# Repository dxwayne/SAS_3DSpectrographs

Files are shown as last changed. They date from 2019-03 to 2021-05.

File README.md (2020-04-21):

# SAS_3DSpectrograps

Next Meeting: 7 April 2020 Meeting ID: 855 133 831

Experiments with spectroscopy using 3D printing.

Zoom meeting and resources, results for this work.

Experiments with spectroscopy using 3D printing.

[Link to Videos on Wiki](https://github.com/dxwayne/SAS_3DSpectrographs/wiki)

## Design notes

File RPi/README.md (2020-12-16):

Raspberry Pi
============

Included herein are various interesting parts and code for the RPi.

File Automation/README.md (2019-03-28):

Good article about motors
--------------------------
https://www.instructables.com/id/Complete-Motor-Guide-for-Robotics/

Robot Parts - example (no experience with company)
https://www.robotshop.com/en/10v-05a-planetary-gear-bipolar-stepper-motor.html#Dimensions
35STH Hybrid Stepping Motor

400 steps per rev
27:1 reduction  = 0.03 degrees per step.

https://ldomotors.manufacturer.globalsources.com/si/6008840349362/pdtl/Stepping-motor/1164961550/nema14-35mm-2phase-hybrid-stepper-motor.htm?state_filt=cn_cnfuj?source=coyname_l4dd
0.9 degree step,

400 steps per rev
27:1 reduction  = 0.03 degrees per step.

https://www.robotshop.com/en/actobotics-84t-aluminum-hub-gear-05.html#Dimensions
Product Code : RB-Sct-682  84T 1/4 inch thick 32 pitch 0.5 bore 2.688 OD

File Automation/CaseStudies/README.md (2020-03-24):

Automation Case Studies
=======================

Collection of basic case studies to allow development of a common architecure of hardware
software for instrument and site automation.

1) Focus on each task to be done like turn the cal lamp on,
   turn the call lamp off, etc,

2) To develop a few bits of code for each function that will include
   a class/code for that task to run in both python and C++.

3) Each task will have messages for actions and to report both
   status, warnings and errors.

I want to ignore the transport layer as much as possible. I like
RS-232 for the OTA and any other standard for the rest of the world.

Sugest dividing the world into telescope/instrumentation, observatory
control, and then to the sensors for temperature, humidity and
other factors as they come along.

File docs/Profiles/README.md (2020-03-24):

Printing Profile Collection
============================

Put the material, vendor etc in this document as a table of contents.

Tony Rodda - Cura Wanhao i3 Plus, with modest mods and some maintenance over time.

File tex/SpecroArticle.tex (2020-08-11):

\documentclass[letter,11pt,oneside]{article}
%%% HEREHEREHERE
%%% APPENDIX
%%% (insert (format "%s" (buffer-file-name)))
% /home/wayne/git/external/SAS_3DSpectrographs/tex/SpecroArticle.tex
%%% (occur "\\(\\\\[a-z]*section\\|appendix\\|input\\|\\<include\\>\\)")

%%\documentclass[11pt,twocolumn]{article}
%%\usepackage[inline]{asymptote}       %% Inline asymptote diagrams
%%\usepackage{wglatex}                 %% Use this one and kill others.
\usepackage{color}                     %% colored letters {\color{red}{{text}}
\usepackage{fancyhdr}                  %% headers/footers
%%\usepackage{fancyvrb}                %% headers/footers
\usepackage{datetime}                  %% pick up tex date time 
\usepackage{lastpage}                  %% support page of ...lastpage
\usepackage{times}                     %% native times roman fonts
\usepackage{textcomp}                  %% trademark
\usepackage{amssymb,amsmath}           %% greek alphabet
\usepackage{parskip}                   %% blank lines between paragraphs, no indent
\usepackage{shortvrb}                  %% short verb use for tables
\usepackage{lscape}                    %% landscape for tables.
\usepackage{longtable}                 %% permit tables to span pages wg-longtable
\usepackage{multicol}                  %% Enhance footnotes/endnotes
\usepackage{url}                       %% Make URLs uniform and links in PDFs
\usepackage{enumerate}                 %% Allow letters/decorations for enumerations
\usepackage{endnotes}                  %% Enhance footnotes/endnotes
\usepackage{listings}                  %% Make URLs uniform and links in PDFs
\pdfadjustspacing=1                    %% force LaTeX-like character spacing
\usepackage{geometry}                  %% allow margins to be relaxed
%%\usepackage{wrapfig}                 %% permit wrapping figures.
%%\usepackage{subfigure}               %% images side by side.
\geometry{margin=1in}                  %% Allow narrower margins etc.
\usepackage[T1]{fontenc}               %% Better Verbatim Font.
\renewcommand*\ttdefault{txtt}        %% 
\usepackage[colorlinks=true]{hyperref} %% Make huperlinks within a PDF
\usepackage{natbib}                    %% bibitems

%% include background image (wg-document-page-background) 

\usepackage{graphic
x}            %% Include pictures into a document
%% (wg-texdoc-inserttikz)

\usepackage{pgf,tikz,pgfplots}
\pgfplotsset{compat=1.15}
\usepackage{mathrsfs}

\usetikzlibrary{decorations.pathreplacing}
\usetikzlibrary{decorations.markings}
\usetikzlibrary{calc}
\usetikzlibrary{arrows}
\pgfplotsset{every tick label/.append style={font=\tiny}}

\newcommand{\degre}{\ensuremath{^\circ}}
\definecolor{qqwuqq}{rgb}{0,0.39215686274509803,0}
\definecolor{qqqqff}{rgb}{0,0,1}
\definecolor{uuuuuu}{rgb}{0.26666666666666666,0.26666666666666666,0.26666666666666666}
\definecolor{ududff}{rgb}{0.30196078431372547,0.30196078431372547,1}
\definecolor{ffqqqq}{rgb}{1,0,0}
\definecolor{xdxdff}{rgb}{0.49019607843137253,0.49019607843137253,1}

\def\documentisdraft{NOTDRAFT}

%% (wg-texdoc-isdraft)

\def\drafttest{DRAFT}
\def\wgdocdate{01 Aug, 2020}
\def\wgdocdatetime{\wgdocdate at \currenttime}
\ifx\documentisdraft\drafttest
\usepackage[left]{lineno}   %%%%%%%%%%%%% DRAFT
\usepackage{draftwatermark}
%%\SetWatermarkScale{5.0}
%%\SetWatermarkColor[gray]{0.3}
\fi

%% (wg-texdoc-insert-fancy-headers)

%%\usepackage[bookmarks]{hyperref} %% Make huperlinks within a PDF
%%\usepackage{makeidx}             %% Make an index uncomment following line
%%\makeindex                       %%.. yeah this one, too. index{key} in text
%%

\newcommand{\taninv}{Tan^{-1}}
\definecolor{verbcolor}{rgb}{0.6,0,0}
\definecolor{darkgreen}{rgb}{0,0.4,0}
\newcommand\debate[1]{\textcolor{darkgreen}{DEBATE: #1} \marginpar{\textcolor{red}{DEBATE} }}
\newcommand{\ltodo}[2]{\marginpar{\textcolor{red}{ACTION: #1}\endnote{#2}}}
\renewcommand{\thefigure}{\thesection-\arabic{figure}}
\newcommand{\menu}{\ensuremath{\;\rightarrow\;}}
\newcommand{\dhl}[1]{{\color{verbcolor}{\texttt#1}}}
\definecolor{wglightgreen}{rgb}{0.88, 0.58, 0.88}
\newcommand{\wgtextbox}[1]{\noindent\fcolorbox{darkgreen}{wglightgreen}{%
    \minipage[t]{\dimexpr0.80\linewidth-2\fboxsep-2\fboxrule\relax}
        {#1}
    \endminipage}}
%%(wg-add-inline-images)  %% add inline images to the mix

%%Begin User Definitions: Hint: ~/.latex.defs and  latex.defs  
%%End User Definitions:
%% (wg-texdoc-adjust-paper-width)
%% (wg-texdoc-insert-hypersetup)
%% (wg-latex-tablet-page)

%%%%%%%%%%%%%%%%%%%%%%%%%%%%%%%%%%%%%%%%%%%%%%%%%%%%%%%%%%%%%%%%%%%%%%%%%%%%%

\begin{document}

%% (wg-latex-pretty-title-page)
%% (wg-texdoc-titleblock)

\title{Letter:\\
Spectrographic Calibration\\
~ \\
{\large Flood vs Beam vs On Axis \\
Injection of Calibration References}}
\author{Wayne Green, Jerry Foote, Clarke Yeager, Anthony Rodda}
\date{\today}
\maketitle

\begin{abstract}
This letter reports preliminary results with spectrographic
calibration of small telescope spectrographs. We have experienced
thermal expansion and mechanical flexture. We are investigating using
a converging beam with the same f/ratio and PSF as a star. This is
proving hard to do. Recent discussions has brought us to consider the
problem from several aspects. These results mainly center on the
LOWSPEC family of spectrograph by Paul Gerlach.

\end{abstract}

%%%%%%%%%%%%%%%%%%%%%%%%%%%%%%%%%%%%%%%%%%%%%%%%%%%%%%%%%%%%%%%%%%%%%%%%%%%%%
%% table of contents
%%%%%%%%%%%%%%%%%%%%%%%%%%%%%%%%%%%%%%%%%%%%%%%%%%%%%%%%%%%%%%%%%%%%%%%%%%%%%
 
\pagenumbering{roman}   % i,ii,etc
%%\pagenumbering{gobble}   %ignore page numbers for a while
\pdfbookmark[0]{Table of Contents}{MyTOC} % if usepackage{hyperref} in use.
\tableofcontents
%\listoffigures
\listoftables
\newpage

\setcounter{section}{0}
\pagenumbering{arabic}

\ifx\documentisdraft\drafttest
\linenumbers    %%%%%%%%%%%%% DRAFT
\fi

\section{Overview}

For about 18 months the cohort suffered Green saying to ignore the
signal and focus on the noise. If noise is kept under acceptable
control -- the science result's signal can be shown to be
objectively better. 

One critical source of ``noise'' is calibration line shift, accuracy,
usefulness in the recent Spectro-L thread.

The short question is between utilizing a gas lamp for reference
calibration lines by flooding a slit (flood) or using a precisely
formed converging beam (beam). The Question come down to the quality
of lines made by the lamp, and how does the impact of a simple
experiment of subtracting the first comp image from the last comp
image -- assuming one has followed a strategy along the lines of 1)
comp-sci-sci-sci-comp or 2) comp-sci-comp-sci-comp-sci-comp. Flats
have important questions of their own but are not germane to this
question.

IRAFs answer to how to subtract images comp1.fits from comp2.fits:
\dhl{imarith comp1 - comp2 diff.fits}. We've seen shifts of several
pixels across one observation.

Answering the difference between flood vs beam,. first start with
the ``thin lens equation''\footnote{The ``lens makers formula'' deals with
the radius of curvature for lens surfaces. Appendix \ref{sec:lensmakersformula}.}:

\begin{figure}[h!]
\centering
\input{images/LMF2.tikz}
\caption{Lens Makers Formula with star and cal-lamp light. (Not happy
with the rendering -- Tikz needs upgrading.)}
\label{fig:LMF}
\end{figure}

\begin{align}
\frac{1}{f} &= \frac{1}{s_{1}} +  \frac{1}{s_{2}} 
\end{align}

where f is the actual focal length of the lens/lens assembly for
infinity ; $s_{1}$ is the
distance from the lens to the target and $s_{2}$ is the distance from
the lens to the virtual image.

A few waypoints to
notice: if $s_{1}$ is essentially at infinity, then $\frac{1}{s_{1}}$
goes to zero and the position $s_{2}$ is equal to the stated focal
length. The next very interesting thing is that if a light is placed
at $s_{2}$ (L--D not shown), the beam is essentially parallel -- or at
infinity and is said to be collimated.

In Fig. \ref{fig:LMF} there should be a lens indicated along C--K--D
that did not render.  In the spectrograph, the slit is at $f_{1}$.
The arrow is an off-axis near-field bulb filiment, producing a ray
Lamp\menu D \menu M, where the star's ray, along the same path, is
from infinity \menu D \menu ${f_{1}}$. The two angles are not the
same. Taking a bundle of lines along the filiment of the lamp produces
a series of rays -- each with a different angle. Variation in the
position of the lamp can cause a mis-match of calibration
locations. There is also a bias from the position of the bulb
w.r.t. the slit.

If $s_{1}$ is close to the lens, then the rays are diverging into the
lens and come to focus at $s_{2}$ some distance farther out than the
focal length of the lens. The angle of the rays fall within the
range subtended by the geometry of the circle or rays hitting the lens
surface. A wider range, the closer the source to the lens. 

A critical thing to remember, is that the target itself (size of the
bulb -- say the two electrodes) causes a mix of angles of rays in the
bulb's beam. This adds up to more variance in incidence angles at the
grating.

Flooding has diverging beams, acts like a ``near-field'' target and
therefore the focus of the collimator is wrong w.r.t. a grating. By
the grating equation, this generates a diverging beam at the grating
-- the incidence angle of rays at the 'right' side will be different
than those from the 'left' side. This in essence effects the focus.
Flooding off axis produces an asymmetry in the output of the
collimator and will produce a ``corresponding'' shift in the lens. The
asymmetry is introduced by changes due to thermal expansion and with
flexure.  Focusing with the comp lamp is invalid. Focusing with sky
lines late in afternoon is much better.

For reference, the grating equation for a reflection grating:

\begin{align}
\frac{m\lambda}{d} &= sin(\alpha) + sin(\beta)
\end{align}

where $m$ is the mode, $\lambda$ in wavelength, $\alpha$ is the
``angle if incidence'' and $\beta$ is the ``angle of diffrection''.
The near-field lamp produces a wide range of $\alpha$ incidence angles
that are not consistent with the far-field stellar image. The addition
operator needs to be subtraction for transmission gratings.

\textbf{\emph{Summary 1:}} Co-linear rays from the collimator to the grating improves
the overall placement, line shape, and line width (focus) of the resulting
spectra. Repeatable variations will produce a systematic wavelength
identification. Non-repeatable variations due to variations in temperature
and flexure introduce random wavelength positions.

\subsection{Mitigation Strategies}

Use a diffusing screen. This converts more coherent (not very coherent
to begin with straight from the bulb) into a ``Lambertian'' source.
The Lambertian source is usually depicted with a single point and 
speaks to the intensity at different angles projected away from that point.
Integrating over all points boils down to a large mix of rays at different
angles.

\textbf{\emph{Summary 2:}} One can argue the narrow width of the slit mitigates the
use of a flooding lamp, but measurements shows a small shift -- one
that can amount to 10s to 1000s of km s-1 in the spectra.

\textbf{\emph{Summary 3:}} With energy  $E=h\nu$ relates to wavelength ($lambda$)
as $\nu = c/\lambda$, a shift in wavelength improperly converted
to the targets frame of reference amounts to a misstatement of
Energy. This is not accounted for through the line ratio analysis
process.

\textbf{\emph{Summary 4:}} It is obvious that radial velocity statements mis-stated
as the $\Delta{\lambda}$ is non-linear and a shift due to mis-identification
will have a material impact on radial velocity statements.

Mitigation by solving a spectrum using sky-lines or using the absorption
features in the target itself (within the targets frame of reference)
will help with line ratios. Solving with both sky-lines and with
the target gives the shift needed to state the radial velocity.

\subsection{Beam Case}

Great idea, difficult to implement. The general idea is a diffusion
method (scattering screen, microlenses, integrating sphere), a 
collimator, a matching f/ratio lens for the star's image and
a way to match the injection angles. Its the injection matching
that is proving mechanically difficult.

\section{Conclusion}

The use of comp lamps may be done away with if sufficient information
in the form of sky-lines (light pollution and tellurics). Nodding
the telescope and employing a sufficient exposure time can solve
the flood vs beam question. In may cases, small telescope spectroscopy
is well suited to detect and report gross changes of state with 
a target, and to help qualify novae. Novae respond well to low
SNR and to very low R values. We have ignored many issues in this
discussion that bear thought.

\appendix
\renewcommand \thesection{\Alph{section}}

\section{Science Objectives}

The quintessential aspects of spectral reduction boils down to the
energy physics represented by effective feature width or the centroid
of a target's features for radial velocity study. Small telescope
spectrographs are in the R$\sim$ 600,1000,10000 range, generically
for the Alpy, Lisa and LHires/echelle products from Shelyak.
The prominent features include H$\alpha$ or nova lines. R is
essentially $\Delta{\lambda}/\lambda$, and for H$\alpha$ of
say 6000\AA\; then the Alpy should have a 10\AA\; resolution.

\begin{align}
R &= \frac{\lambda}{\Delta{\lambda}} \\
\frac{\Delta{\lambda}}{\lambda} &= \frac{\Delta{\nu}}{\nu} = \frac{v}{c} \\
v &= \frac{c}{R}
\end{align}

Here, a gross simplification using H$\alpha$ as 6000\AA\;, 

\begin{table}[h!]
%\phantomsection
%\addcontentsline{toc}{section}{ TOC CAPTION}
% \setlength{\belowcaptionskip}{6pt} % adjust space under caption abovecaptionskip
% \renewcommand{\arraystretch}{1.3} % adjust line spacing
%\small{
%\begin{minipage}{\textwidth}     % for footnotes in table.
%\caption[TOC]{Gross Velocity in terms of Resolution R.}
\centering
\begin{tabular}{| r | r |}
%\MakeShortVerb{\|}
%\multicolumn{n}{fmt}{text for merged cols}
\hline
R      & v ( km s-1)    \\ 
\hline
600    & 500    \\ 
1000   & 300    \\ 
10000  & 29    \\ 
%% ones-based: \cline{a-b}
\hline
%%\DeleteShortVerb{|}
\end{tabular}
%%\end{minipage}    %% for footnotes  r@{.}l 
\caption{Gross Velocity in terms of Resolution R}
\label{table:GrossVelocityintermsofResolutionR}
%%} % end small etc
\end{table}

% (iv (setq tmp (mapcar (lambda (a) (/ constant-c a 1e5)) '(600.0 1000.0 10000.0) )))
%    (499.65409666666665 299.792458 29.9792458)

The spectrograph consists of essentially three parts: 1) the
telescope,  2) the slit and 3) the spectrograph's optics.

The slit samples the ``focal plane'' from the telescope, a virtual
image, at point of focus.  The focus in the point of convergence for a
bundle of rays from a science target (star, chunk of nebula, sky
etc). The ray bundle is described well enough by the f/ratio of the
main telescope. Oversimplifying, it is a consistent converging bundle
of rays.

Other aspects that are often ignored include coma (off-axis aspect of
where the slit position falls w.r.t.  the telescope's curved focal
plane) and other attendant astigmatisms. The so called focal ``plane''
is actually curved -- unless flattened by additional optics. See
\citep{1898AJ.....19...17S} for mind numbing details. A flat plane is
common with Ritchey-Crit\'erion telescopes and to a high degree with
the CDK telescopes. Refractors, prone to field curvature will have
Petzval correctors, or may use other flatteners. Newtonians may use a
``Paracor'' \texttrademark or other optics. Longer focal lengths
suffer less but carry larger spot sizes for stars.

Also note the date of Schaeberle's publication. Schaeberle's concerns
center on the fact that most casual thought centers on the principle
ray along the optical axis.

The shape of this focal plane, and the field's energy contribution to
each point on the focal plane surface is way to complicated to delve
into here. The simplifying assumption is that the slit is tiny w.r.t.
the surface; the desired image is tightly defined by the f/ratio's
converging beam and aberrations can be ignored within an appropriate
over-simplifying assumption. Assumption about 'out of focus' rays
often miss the fact that the rays do not have the same f/ratio as the
desired science image and that those contributions (mainly sky in the
general case here) are axi-symmetric. They fail to become collimated,
and present focus and shift issues for use with spectral calibration.

The injection of the cal and flat lamps do not necessarily
satisfy these conditions. The main problem appears to be the
issue of rays from the cal lamp are off-axis, non axi-symmetric,
do not collimate in the same fashion as the science image
and therefore present a range of angles of incidence at the
grating. This in turn presents a range (both focus and shift)
in the lines at the camera's sensor. We have measured this
effect with simple experiments with the LOWSPEC spectrograph.

Our main issue with the LOWSPEC is flexure and thermal expansion.
To minimize these issues we are currently re-conducting the
experiment in a more temperature controlled setting using
stiff aluminum breadboards to host the LOWSPEC 3D printed
optics.

Most SCTs are a train-wreck of design trade-offs. Richard Berry
did a white paper that shows the best optical performance is
only about 125mm behind the telescope. This distance is quite
short. This means inserting guiders is a bit of bother.

A key problem of mismatching the f/ratio of the incoming beam w.r.t.
to a spectrograph's collimating lens/mirror is the slit is now
out of focus, and producing a range of angles of incidence
to the grating. The focus mismatch has the effect of skewing
these angles w.r.t. the position of the slit and optical axis.

The answer, for LOWSPEC, is to provide a prescription for the
collimating lens and to accommodate the lens. The distance
from the collimator to the grating is flexible -- the distance
to the slit is not. 

\section{The lens makers' formula (for completeness)} \label{sec:lensmakersformula}

\begin{subequations}
\begin{align}
P_{\tt{lens}} &= \frac{n_{\tt{lens}} - n_{0}}{n_{o}} \left( \frac{1}{R_{1}} - \frac{1}{R_{2}} \right) \\
\Phi{\lambda} &= \exp\left(\frac{2\pi i}{\lambda} \frac{r^2}{2f}\right) & \tt{phase} \label{eq:hob}
\end{align}
\end{subequations}

where $P_{\tt{lens}}$ is the ``Power'' in diopters, $n$ is the index
of refraction, $R_{1}$ is the radius of the ``front'' of the lens and
$R_{2}$ is the radius of the ``back'' of the lens. Equation
\eqref{eq:hob} wrecks merry-hob in terms of chromatic aberration --
another name for different wavelengths of light coming to focus at
different points, or with different angles of incidence.

\section{Magnitude Drop with Beam Splitter}

There is a commercial spectrograph that uses a beam splitter. Assuming
a 90\% transmission a 10\% loss amounts to 0.114.

\begin{align}
\Delta\:{\tt{mag}} &= -2.5 \frac{\Delta{I}}{1} \\
    0.114\; \tt{mag} &= -2.5 \times log_{10}(.90)
\end{align}

Along the beamsplitter's 10\% axis, injecting a conforming beam gives more
control over the exposure time and better photon statistics. 

% (iv (setq tmp (* -2.5 (log10 .90) )))   0.114

\section{Mirror Makers Formula}

There is a sign switch due to reflection washing around in this
one.

The lens makers formula's analog for mirrors \citep{hyperphysics-mirror}:

\begin{align}
\frac{1}{s_{1}} + \frac{1}{f} &= \frac{1}{s_{2}} 
\end{align}

where $f$ is the focal length of the mirror, $s_{1}$ is the distance
to the 'target' and $s_{2}$ is where the image is formed. Remember it
reverses direction along the optical axis.

%%% ADDAPPENDIX

%% use a bibitem approach to the references publications etc.
%% (wg-bibitem)

%%\clearpage
\addcontentsline{toc}{section}{References}
\renewcommand*{\refname}{References}
\bibliographystyle{apalike}	% bibliographystyle{apalike} and \usepackage{natbib}
\bibliography{SpecroArticle}{}	% expects file "MasterBib.bib"

%%\begin{thebibliography}{80}
%%\usepackage{natbib}   %% bibitems
%%\end{thebibliography}

%%\clearpage
%%\addcontentsline{toc}{section}{Index}
%%\printindex %% www.cs.usask.ca/resources/tutorials/latex/notes/toc-index.pdf

% /home/wayne/git/external/SAS_3DSpectrographs/tex/SpecroArticle.tex

%% (wg-texdoc-endnotes)
\end{document}

-----------------------------------------------------------------------------

Lets consider a optical setup where the $(X,Y)$ plane is along
the objective surface plane and $Z$ axis is the optical axis.
Lets assume axi-symmetric optics and ignore the $X$ axis.
So a piece of paper carrying a diagram consists of $Z$ in
the left-right direction and $Y$ in the up-down direction.

The telescope forms an image that is not necessarily along the optical
$Z$ axis. Best case, the optical axis is part of a perfectly aligned
telescope with a symmetrical Point Spread Function (PSF).  Coma is
introduced for stars off axis -- considered here to be some offset
above or below the $Z$ axis. Now consider the coma as being an
asymmetric beam passing into a slit location off-axis from the main
axis. Lets ignore all astigmatisms other than the coma.

The incoming beam from the telescope is at some f/ratio that is

\begin{align}
\tt{f/ratio} &= \frac{D}{fl} \\
\theta &= \taninv\frac{D}{fl}
\end{align}

My point comes with reconciling the incoming angles of incidence
w.r.t. the grating equation at the grating with the light from
the slit passing through the collimating lens. Up until now,
I have been discounting the significance of matching the f/ratio
of the collimating lens to the PDF of the telescope. 

Discussions with Bob Buchheim, SAS, has brought the FITS multispec
format to his attention, A Multispec file (several different bands of
equispec data) carries noise together with the spectrum each with its
own NAXIS. Discussions with Forrest Sims and Buchheim brought the
utility of storing image data for the reduced science image, the
calibration (comp) image and a sky band in a FITS
Multi-Extension-Format (MEF) format. I have been using both for years,
even bolting MEF into PyRAF with a few lines of Python for my personal
startup code. I have been promoting publishing properly flux
calibrated images using the multispec format.

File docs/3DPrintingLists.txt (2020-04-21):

3D Printing YouTube Listing (obviously not all inclusive but a fun start)

YouTube Name/search phrase
---------------------------
Thomas Sanladerer
CHEP
3D Now
Perusals 3D by Josef Prusa
teaching tech
electronoobs	(fun with lots of electronic and other projects as well)
3D Printing Nerd

Web sites for pre-made models to print:
thingiverse		(This also has lots of 3D Printing videos on YouTube)
yeggi
myminifactory	(This also has lots of 3D Printing videos on YouTube)

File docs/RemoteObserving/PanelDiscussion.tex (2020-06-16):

\documentclass[letter,11pt,oneside]{article}

%%% (occur "\\(\\\\[a-z]*section\\|appendix\\|input\\|\\<include\\>\\)")

%%\documentclass[11pt,twocolumn]{article}
%%\usepackage[inline]{asymptote}   %% Inline asymptote diagrams
%%\usepackage{wglatex}             %% Use this one and kill others.
\usepackage{color}               %% colored letters {\color{red}{{text}}
\usepackage{fancyhdr}            %% headers/footers
%%\usepackage{fancyvrb}            %% headers/footers
\usepackage{datetime}            %% pick up tex date time 
\usepackage{lastpage}            %% support page of ...lastpage
\usepackage{times}               %% native times roman fonts
\usepackage{textcomp}            %% trademark
\usepackage{amssymb,amsmath}     %% greek alphabet
\usepackage{parskip}             %% blank lines between paragraphs, no indent
\usepackage{shortvrb}            %% short verb use for tables
\usepackage{lscape}              %% landscape for tables.
\usepackage{longtable}           %% permit tables to span pages wg-longtable
\usepackage{url}                 %% Make URLs uniform and links in PDFs
\usepackage{enumerate}           %% Allow letters/decorations for enumerations
\usepackage{endnotes}            %% Enhance footnotes/endnotes
\usepackage{listings}            %% Make URLs uniform and links in PDFs
\pdfadjustspacing=1                %% force LaTeX-like character spacing
\usepackage{geometry}            %% allow margins to be relaxed
%%\usepackage{wrapfig}             %% permit wrapping figures.
%%\usepackage{subfigure}              %% images side by side.
\geometry{margin=1in}            %% Allow narrower margins etc.
\usepackage[T1]{fontenc}         %% Better Verbatim Font.
\renewcommand*\ttdefault{txtt}   %% 
%%\usepackage{natbib}   %% bibitems

%% include background image (wg-document-page-background) 

\usepackage{graphicx}            %% Include pictures into a document
%% (wg-texdoc-inserttikz)

\def\documentisdraft{NOTDRAFT}

%% (wg-texdoc-isdraft)
%% (wg-texdoc-insert-fancy-headers)

%%\usepackage[bookmarks]{hyperref} %% Make huperlinks within a PDF
%%\usepackage{makeidx}             %% Make an index uncomment following line
%%\makeindex                       %%.. yeah this one, too. index{key} in text
%%

\definecolor{verbcolor}{rgb}{0.6,0,0}
\definecolor{darkgreen}{rgb}{0,0.4,0}
\newcommand\debate[1]{\textcolor{darkgreen}{DEBATE: #1} \marginpar{\textcolor{red}{DEBATE} }}
\newcommand{\ltodo}[2]{\marginpar{\textcolor{red}{ACTION: #1}\endnote{#2}}}
\renewcommand{\thefigure}{\thesection-\arabic{figure}}

%%(wg-texdoc-adjust-paper-width)%%Begin User Definitions: Hint: ~/.latex.defs and  latex.defs  
%%End User Definitions:

%% (wg-texdoc-insert-hypersetup)

%%%%%%%%%%%%%%%%%%%%%%%%%%%%%%%%%%%%%%%%%%%%%%%%%%%%%%%%%%%%%%%%%%%%%%%%%%%%%

\begin{document}

%% (wg-latex-pretty-title-page)
%% (wg-texdoc-titleblock)

\setcounter{section}{1}
\pagenumbering{arabic}

\ifx\documentisdraft\drafttest
\linenumbers    %%%%%%%%%%%%% DRAFT
\fi

Hi,

\vskip 1cm

\begin{quote}{\centering {\Large

I'm am inviting you\\
 yes you\\
 to be a member of the SAS panel discussion on \\
``Remote Observatories for Small-Telescope Science''\\

taking place at the SAS Symposium in Ontario\\
 Friday afternoon 31 May. 2019 \\
at 4:00 PM --- 'till'. \\

}}
\end{quote}
\vskip 1cm

We placed the discussion last on the agenda. While planning for 1 hour
it can be allowed to run long.

Below is a list of the basic topics off the top of my head, please
add and delete as you see fit.

I am approaching this Panel as a 'blank slate'. If you wish to
participate please let me know ASAP -- then take some time to pull
together and send me questions you feel are important to the
discussion.  We plan to have a power-point available. We will
take questions primarily from the audiance.

If you have information that can fit into slides I will create an
overall PPT presentation with hyper-links so we can call upon the
slides as needed at various points during the discussion.

The implicit goal of the panel is to encourage an ongoing discussion
to promote best-practices of small-telescope remote operation and to
avoid a one-prescription fits all answer.

I will be the moderator. I will not be involved in the answers but
will serve to keep the discussion moving along. 

We want to include hilarious mistakes to avoid, disasters to celebrate,
and to avoid one-prescription fits all answers.

Experience is a good teacher. Somebody else's experience is a better
teacher!

Sincerely, Wayne Green

+1.303.818.1290 \\
dxwayne@gmail.com

\subsection{Broad Initial Topics}

\vspace{-.15cm}
\begin{enumerate}\addtolength{\itemsep}{-0.5\baselineskip}
   \item   First off
\vspace{-.15cm}
\begin{enumerate}\addtolength{\itemsep}{-0.5\baselineskip}
   \item   Experience Level
   \item   Buy
   \item   Build
   \item   Interoperability
   \item   INDI vs ASCOM
   \item   Planetarium Software
   \item   Planning
\vspace{-.15cm}
\begin{enumerate}\addtolength{\itemsep}{-0.5\baselineskip}
   \item   Software
   \item   Web resources
   \item   catalogs
   \item   database
\end{enumerate}

   \item   Raw Target List
\end{enumerate}
\end{enumerate}

%%%%%%%%%%%
\vspace{-.15cm}

\begin{enumerate}\addtolength{\itemsep}{-0.5\baselineskip}
\setcounter{enumi}{1}
   \item   Health and Safety
\vspace{-.15cm}
\begin{enumerate}\addtolength{\itemsep}{-0.5\baselineskip}
   \item   Battery burns the house down
   \item   Lightening
   \item   Its Dark!
   \item   Its Cold!
   \item   Its Dirty!
   \item   Its Quiet
\vspace{-.15cm}
\begin{enumerate}\addtolength{\itemsep}{-0.5\baselineskip}
   \item   Cameras/audio
\end{enumerate}

   \item   Thermal Expansion
\vspace{-.15cm}
\begin{enumerate}\addtolength{\itemsep}{-0.5\baselineskip}
   \item   Cable Flexibility
   \item   Heat/Cold loosening connections
   \item   Electrical intermittants
   \item   Grease thermal range
\end{enumerate}

   \item   Its Hot!
   \item   Near-by human to fix/protect things
\end{enumerate}

%%%%%%%%%%%
\end{enumerate}

\vspace{-.15cm}
\begin{enumerate}\addtolength{\itemsep}{-0.5\baselineskip}
\setcounter{enumi}{2}
   \item   Telescopes - align/clean/thermal expansion
\vspace{-.15cm}
\begin{enumerate}\addtolength{\itemsep}{-0.5\baselineskip}
   \item   OTA
   \item   Platescale
\end{enumerate}
\end{enumerate}

\vspace{-.15cm}
\begin{enumerate}\addtolength{\itemsep}{-0.5\baselineskip}
\setcounter{enumi}{3}
   \item   Mounts
\vspace{-.15cm}
\begin{enumerate}\addtolength{\itemsep}{-0.5\baselineskip}
   \item   German, Fork-Equitorial, Nasmyth
   \item   Alignment (field rotation)
   \item   Limit Switches
   \item   Home-position feedback
   \item   Encoders
   \item   Weight/Balance/Inertia
\end{enumerate}
\end{enumerate}

\vspace{-.15cm}
\begin{enumerate}\addtolength{\itemsep}{-0.5\baselineskip}
\setcounter{enumi}{4}
   \item   Targets
\vspace{-.15cm}
\begin{enumerate}\addtolength{\itemsep}{-0.5\baselineskip}
   \item   Acqiisition
   \item   Verify
   \item   Guiding
\end{enumerate}
\end{enumerate}

%%%%%%%%%%%
\vspace{-.15cm}
\begin{enumerate}\addtolength{\itemsep}{-0.5\baselineskip}
\setcounter{enumi}{5}
   \item  Software
\vspace{-.15cm}
\begin{enumerate}\addtolength{\itemsep}{-0.5\baselineskip}
   \item   Communications
\end{enumerate}

\vspace{-.15cm}
\begin{enumerate}\addtolength{\itemsep}{-0.5\baselineskip}
   \item   WiFi
   \item   EFI (Electronic Noise)
   \item   Interface
\begin{itemize}
\addtolength{\itemsep}{-0.5\baselineskip}
   \item   Teamviewer
   \item   VNC
\end{itemize}

   \item   NTPD Time Sync
   \item   File Export
\begin{itemize}
\addtolength{\itemsep}{-0.5\baselineskip}
   \item   Preprocess with pipelines
   \item   SSH/Putty
   \item   SFTP
   \item   Git
\end{itemize}
\end{enumerate}

   \item   Windows/Linux/Mac
\vspace{-.15cm}
\begin{enumerate}\addtolength{\itemsep}{-0.5\baselineskip}
   \item   Commercial
   \item   Custom
\end{enumerate}

   \item   SoC
\vspace{-.15cm}
\begin{enumerate}\addtolength{\itemsep}{-0.5\baselineskip}
   \item   Pi
   \item   Arduino
   \item   Distributed/Integrated
\end{enumerate}

   \item   Mounts
\vspace{-.15cm}
\begin{enumerate}\addtolength{\itemsep}{-0.5\baselineskip}
   \item   Control/Recovery
\end{enumerate}

   \item   Controls:
\vspace{-.15cm}
\begin{enumerate}\addtolength{\itemsep}{-0.5\baselineskip}
   \item   open-loop
   \item   closed-loop
\end{enumerate}

   \item   Sensors:
\vspace{-.15cm}
\begin{enumerate}\addtolength{\itemsep}{-0.5\baselineskip}
   \item   Usual:
\end{enumerate}

\begin{itemize}
\addtolength{\itemsep}{-0.5\baselineskip}
   \item   Zeros/darks/flats (not why but scheduling)
   \item   Dome flats/twilight flats
\end{itemize}

   \item   Cameras and Filters
\vspace{-.15cm}
\begin{enumerate}\addtolength{\itemsep}{-0.5\baselineskip}
   \item   Focus
   \item   Control/Recovery
\end{enumerate}

   \item   Spectrographs
\vspace{-.15cm}
\begin{enumerate}\addtolength{\itemsep}{-0.5\baselineskip}
   \item   Control/Recovery
   \item   Comparison lamps
\end{enumerate}

   \item   Dome vs Roll-off
   \item   Mechanical Topics
\vspace{-.15cm}
\begin{enumerate}\addtolength{\itemsep}{-0.5\baselineskip}
   \item   Motors
   \item   Grease
\end{enumerate}

   \item   Power Quantity/Quality
\vspace{-.15cm}
\begin{enumerate}\addtolength{\itemsep}{-0.5\baselineskip}
   \item   UPS
   \item   Standalone Batteries
\end{enumerate}

   \item   Weather
\vspace{-.15cm}
\begin{enumerate}\addtolength{\itemsep}{-0.5\baselineskip}
   \item   Forecasts
   \item   Monitoring
   \item   Panic
\end{enumerate}
\end{enumerate}

\section{John Hout}

John Hout

Addition Remote astronomy topics:

\vspace{-.15cm}
\begin{enumerate}\addtolength{\itemsep}{-0.5\baselineskip}
   \item   Periodic Maintenance
\vspace{-.15cm}
\begin{enumerate}\addtolength{\itemsep}{-0.5\baselineskip}
   \item     cleaning - optics, elecctronics, keyboards...
   \item     lubrication
   \item     Balance
   \item     Desicants
   \item     UPS's
   \item     Spares Inventory
   \item     Anticipate
\vspace{-.15cm}
\begin{enumerate}\addtolength{\itemsep}{-0.5\baselineskip}
   \item        Failures
   \item        Obsolesence
   \item        Software Support Withdrawl
\end{enumerate}
\end{enumerate}

   \item   Infrastructure
\vspace{-.15cm}
\begin{enumerate}\addtolength{\itemsep}{-0.5\baselineskip}
   \item      Communication
   \item      Phone
   \item      Radio/Microwave
   \item      Internet
   \item         Ethernet
   \item         Wifi
   \item         Fiber
   \item         Routers
   \item         Security
\vspace{-.15cm}
\begin{enumerate}\addtolength{\itemsep}{-0.5\baselineskip}
   \item            VPNs
   \item            SSH
   \item            Firewalls
\end{enumerate}

   \item         DHCP-DNS Servers
   \item     Communications Failure/Recovery
\end{enumerate}

   \item   Power
\vspace{-.15cm}
\begin{enumerate}\addtolength{\itemsep}{-0.5\baselineskip}
   \item      On grid/Off Grid
   \item      Batteries
   \item      UPS's
   \item      Remote outlet Switching
   \item      Power Failure Management/Recover
   \item      Mounts
\vspace{-.15cm}
\begin{enumerate}\addtolength{\itemsep}{-0.5\baselineskip}
   \item            Plate Solutions
   \item            Focus, Focus, Focus..
   \item            Mutliplexed Instruments on a single mount
\end{enumerate}

   \item   Control Paradigms
   \item      Telepresense
   \item      Scripting
\vspace{-.15cm}
\begin{enumerate}\addtolength{\itemsep}{-0.5\baselineskip}
   \item         Closed/Extensible
   \item         Scripting extension languages
\end{enumerate}

   \item      Scheduling
   \item      Shared/Private Use
   \item      Remote Facility Locale
\vspace{-.15cm}
\begin{enumerate}\addtolength{\itemsep}{-0.5\baselineskip}
   \item         Nearby - minutes
   \item         Distant - hours
   \item         Very Distant - Days
\end{enumerate}

   \item      Distributed Control
   \item   Construction
\vspace{-.15cm}
\begin{enumerate}\addtolength{\itemsep}{-0.5\baselineskip}
   \item      Planning
   \item      Document!!!
   \item      Toolchain Preservation
   \item      Archiving:
\end{enumerate}

\vspace{-.15cm}
\begin{enumerate}\addtolength{\itemsep}{-0.5\baselineskip}
   \item         Never trust a cloud!!!
   \item         Tools
   \item         Software
   \item         Systems
   \item         Rawdata
   \item         Utilities
   \item         Licenses/Keys
   \item         Manuals
   \item         Scripts
\end{enumerate}
\end{enumerate}
\end{enumerate}

%%\appendix
%%\renewcommand \thesection{\Alph{section}}

%% use a bibitem approach to the references publications etc.
%% (wg-bibitem)

%%\clearpage
%%\addcontentsline{toc}{section}{References}
%%\renewcommand*{\refname}{My Bibliography and References}
%%\bibliographystyle{plain}	% bibliographystyle{apalike} and \usepackage{natbib}
%%\bibliography{MasterBib}	% expects file "MasterBib.bib"

%%\clearpage
%%\addcontentsline{toc}{section}{Index}
%%\printindex %% www.cs.usask.ca/resources/tutorials/latex/notes/toc-index.pdf

%%\begin{thebibliography}{80}
%%\usepackage{natbib}   %% bibitems
%%\end{thebibliography}

% /home/wayne/git/pre.SAS2019/PanelDiscussion.tex

%% (wg-texdoc-endnotes)
\end{document}

\begingroup \fontsize{10pt}{10pt}
\selectfont
%%\begin{Verbatim} [commandchars=\\\{\}]
\begin{verbatim} 
Arne Henden     ahenden@gmail.com
Tom Smith       tcsmith88354@gmail.com
Jerry Foote     jfoote@infowest.com
Bob Denny       rdenny@dc3.com
Larry Dingle    larry.dingle47@gmail.com
Stan Watson     Watsons@umich.edu
Steve Bisque    stephen@bisque.com
HOOT John	    observatory@ssccorp.com
\end{verbatim}
\endgroup
%% \end{Verbatim}

ahenden@gmail.com
tcsmith88354@gmail.com
jfoote@infowest.com
rdenny@dc3.com
larry.dingle47@gmail.com
Watsons@umich.edu
stephen@bisque.com
observatory@ssccorp.com

Arne Henden
Tom Smith
Jerry Foote
Bob Denny
Larry Dingle
Stan Watsonx2
Steve Bisque
Hoot John	

Tom Smith:
Here are some things to maybe add:
   - Telescope-optical train f/ratio
   - Mount types, advantages and disadvantages
   - What if my polar alignment isn't perfect, results in images
   - WiFi or Ethernet based communications
   - Flat & calibration lamps for good results
   - Remote desktop, VNC, Anywhere PC, SSH, SFTP, Putty
   - Limit switches on scopes and for observatory control and indication
   - Two-way audio, maybe incorporated into existing webcams
   - UPS
   - Time sync methods
   - Automatic processing pipelines
   - Planning an observation, where to find information
   - Sky catalogs and/or planetarium softwares
   - Guiding, several methods
   - Closed or open loop controls
   - Is someone nearby to assist if things go wrong from remote operating positions
   - Buy or build, experience level and time commitments

- First off
   - Experience Level
   - Buy
   - Build
   - Interoperability
   - INDI vs ASCOM
   - Planetarium Software
   - Planning
      - Software
      - Web resources
      - catalogs
      - database
   - Raw Target List
%%%%%%%%%%%
- Health and Safety
   - Battery burns the house down
   - Lightening
   - Its Dark!
   - Its Cold!
   - Its Quiet
     - Cameras/audio
   - Thermal Expansion
      - Cable Flexibility
      - Heat/Cold loosening connections
      - Electrical intermittants
      - Grease thermal range
   - Its Hot!
   - Near-by human to fix/protect things
%%%%%%%%%%%
- Telescopes
  - OTA
  - Platescale
- Mounts
  - German, Fork-Equitorial, Nasmyth
  - Alignment (field rotation)
  - Limit Switches
  - Home-position feedback
  - Encoders
  - Weight/Balance/Inertia
- Targets
   - Acqiisition
   - Verify
   - Guiding
%%%%%%%%%%%
-Software
   - Communications
      - WiFi
      - EFI (Electronic Noise)
      - Interface
        - Teamviewer
        - VNC
      - NTPD Time Sync
      - File Export
        - Preprocess with pipelines
        - SSH/Putty
        - SFTP
        - Git

   - Windows/Linux/Mac
      - Commercial
      - Custom
   - SoC
      - Pi
      - Arduino
      - Distributed/Integrated
   - Mounts
      - Control/Recovery
   - Controls:
      - open-loop
      - closed-loop
   - Sensors:
      - Usual:
         - Zeros/darks/flats (not why but scheduling)
         - Dome flats/twilight flats
   - Cameras and Filters
      - Focus
      - Control/Recovery
   - Spectrographs
      - Control/Recovery
      - Comparison lamps
   - Dome vs Roll-off
   - Mechanical Topics
      - Motors
      - Grease
   - Power Quantity/Quality
      - UPS
      - Standalone Batteries
   - Weather
      - Forecasts
      - Monitoring
      - Panic

John Hout

Addition Remote astronomy topics:

\vspace{-.15cm}
\begin{enumerate}\addtolength{\itemsep}{-0.5\baselineskip}
   \item   Periodic Maintenance
\vspace{-.15cm}
\begin{enumerate}\addtolength{\itemsep}{-0.5\baselineskip}
   \item     cleaning - optics, elecctronics, keyboards...
   \item     lubrication
   \item     Balance
   \item     Desicants
   \item     UPS's
   \item     Spares Inventory
   \item     Anticipate
\vspace{-.15cm}
\begin{enumerate}\addtolength{\itemsep}{-0.5\baselineskip}
   \item        Failures
   \item        Obsolesence
   \item        Software Support Withdrawl
\end{enumerate}
\end{enumerate}

   \item   Infrastructure
\vspace{-.15cm}
\begin{enumerate}\addtolength{\itemsep}{-0.5\baselineskip}
   \item      Communication
   \item      Phone
   \item      Radio/Microwave
   \item      Internet
   \item         Ethernet
   \item         Wifi
   \item         Fiber
   \item         Routers
   \item         Security
\vspace{-.15cm}
\begin{enumerate}\addtolength{\itemsep}{-0.5\baselineskip}
   \item            VPNs
   \item            SSH
   \item            Firewalls
\end{enumerate}

   \item         DHCP-DNS Servers
   \item     Communications Failure/Recovery
\end{enumerate}

   \item   Power
\vspace{-.15cm}
\begin{enumerate}\addtolength{\itemsep}{-0.5\baselineskip}
   \item      On grid/Off Grid
   \item      Batteries
   \item      UPS's
   \item      Remote outlet Switching
   \item      Power Failure Management/Recover
   \item      Mounts
\vspace{-.15cm}
\begin{enumerate}\addtolength{\itemsep}{-0.5\baselineskip}
   \item            Plate Solutions
   \item            Focus, Focus, Focus..
   \item            Mutliplexed Instruments on a single mount
\end{enumerate}

   \item   Control Paradigms
   \item      Telepresense
   \item      Scripting
\vspace{-.15cm}
\begin{enumerate}\addtolength{\itemsep}{-0.5\baselineskip}
   \item         Closed/Extensible
   \item         Scripting extension languages
\end{enumerate}

   \item      Scheduling
   \item      Shared/Private Use
   \item      Remote Facility Locale
\vspace{-.15cm}
\begin{enumerate}\addtolength{\itemsep}{-0.5\baselineskip}
   \item         Nearby - minutes
   \item         Distant - hours
   \item         Very Distant - Days
\end{enumerate}

   \item      Distributed Control
   \item   Construction
\vspace{-.15cm}
\begin{enumerate}\addtolength{\itemsep}{-0.5\baselineskip}
   \item      Planning
   \item      Document!!!
   \item      Toolchain Preservation
   \item      Archiving:
\end{enumerate}

\vspace{-.15cm}
\begin{enumerate}\addtolength{\itemsep}{-0.5\baselineskip}
   \item         Never trust a cloud!!!
   \item         Tools
   \item         Software
   \item         Systems
   \item         Rawdata
   \item         Utilities
   \item         Licenses/Keys
   \item         Manuals
   \item         Scripts
\end{enumerate}
\end{enumerate}
\end{enumerate}

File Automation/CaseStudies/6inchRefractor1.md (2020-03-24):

Basic 6-Inch LHires3
=====================

6-inch refractor with a Moonlite Express Night crawler focuser and
rotator. It will use a LHires3 spectrograph.

- heat the spectrograph. The spectrograph will have temperatue sensors
  for that purpose.

- focus the spectrograph

- remotely turn on the comp lamp, flat lamp and the slit led.

- a video finder that works when asked

-wider field camera to watch the dome slit that will take a short
  exposure image when asked.

A stretch goal: I want to mount a Apogee U8 + filter wheel and
a Mamiya RB67 lens for patrol of the spectrograph's fields.
This will utilize a Odroid with KStars/INDI

I want a power distribution box with 13+V in and regulated 12/5/3.3
V out.

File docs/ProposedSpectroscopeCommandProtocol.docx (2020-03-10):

# Proposed/Draft Spectroscope Command Protocol

Initiated by Thomas C. Smith

March 10, 2020

The intent of this document is to formalize/standardize the command protocol for use with the various microcontroller devices incorporated into a spectroscope and support equipment, independent of the actual device being commanded. A simple ASCII code/characters will help to provide desperate programs the ability to intercommunicate with a common set of command codes, thereby allowing for modular programming schemes.

************************ LHiRes III lamp control protocol ************************

Command Function

________ _______________________________________________________________________________________

c (ON) calibration relay ONLY

C (ON) calibration relay with associated LED functional

d or D (OFF) calibration relay and LED

f (ON) flat relay ONLY

F (ON) flat relay with associated LED functional

g or G (OFF) flat relay and LED

b (ON) both calibration and flat relays ONLY

B (ON) both calibration and flat relays with associated LEDs functional

a or A (OFF) both relays and LEDs

O Everything OFF

************************ LowRes(x) control protocol ************************

Command Function

________ ________________________________________________________________________________________

LRc (ON) LowRes calibration lamp ONLY

LRC (ON) LowRes calibration lamp AND local LED

LRd or LRD (OFF) LowRes calibration lamp AND local LED

LRf (ON) LowRes flat lamp ONLY

LRF (ON) LowRes flat lamp AND local LED

LRg or LRG (OFF) LowRes flat lamp AND LED

LRLO Every lamp and local LED OFF

LRT1 (Request) temperature device #1 value

LRT2 (Request) temperature device #2 value

LRT3 (Request) temperature device #3 value

LRT4 (Request) temperature device #4 value

LRHOn (ON) heating element

LRHOff (OFF) heating element

LRFIxxxx (IN) main focuser IN xxxx steps (Ex.: LRFI2025 move in 2025 steps)

LRFOxxxx (OUT) main focuser OUT xxxx steps

LRCI (IN) move the calibration lamp mirror IN to program stop

LRCO (OUT) move the calibration lamp mirror OUT to program stop

LRPA (GO TO) horizontal paralactic angle gravity vector, then release

LRRxxx (GO TO) rotator angle xxx (Ex.: LRR120 rotate to 120 degree position)

(It was decided earlier that we need not automate the other focusing devices)

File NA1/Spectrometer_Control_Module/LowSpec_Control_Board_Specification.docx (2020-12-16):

LowSpec Control Board Specification

V01

Clarke Yeager

06/08/2020

Overview:

This is a board that is located in or on the spectrometer. It is designed to operate with the LowSpec and follow-on spectrometer. It’s intent is to work in conjunction with the High Voltage Supply module for the relco lamp and an ODroid architecture described in my earlier Functional Block Diagram – V2.

This is only a first prototype and will have to be modified depending on the end requirement to control the follow on spectrometer.

The Calibration Lamp (Relco lamp) and Flat lamp are controlled from the High Voltage Supply module.

This module controls:

*A high intensity LED is used to illuminate the slit to assist in aligning the target on the slit

* Heating pads for temperature control (if temperature control is used or could be used for other purposes)

* Temperature sensors for feedback on the temperature control

* Two stepper motors for grating rotation and calibration lamp inserter ( as defined but could be used of other purposes)

Power supply requirements:

+5 volts – used for Arduino Nano 33 BLE sense and stepper motors

+12 volts – used for PWM control of the heating pad, slit illumination LED

Function:

- I wanted to implement some sort of feedback so when a command is sent by the ODroid the unit can respond with a signal saying that the command was received and the device is working.
- I use the light sensing capability of the Nano 33 BLE sense module as some of the feedback.
- The slit illuminator is a high intensity LED that could be mounted inside of a spectrometer somewhere or in the bottom of the LowSpec II housing. It could be populated on the board in a location so the control module could be mounted on the bottom of the LowSpec, or it could be hooked up to J6 and wired to where ever is desired. As a feedback mechanism I have a standard LED hooked in series with the high intensity LED. This will put out a small amount of light that can be detected by the light sensor in the Nano 33 BLE sense module. This will light if there is current going through the high intensity LED. This can also be used to monitor if the LED is changing over time.
- The slit illuminating LED is hooked up to one of the IO pins that can be uses as a PWM so it could be used to control the intensity of the illumination if desired.
- The heater output, J7, supplies PWM current to the heating pads if temperature control is implemented. There is a voltage divider driven by the heater output that supplies about 1.5 volts to the analog input A2 when the heater is turned on. This gives feedback that the command to turn on the heating pads functioned properly and that current is flowing through the heating pads.
- The temperature of the heat control can be set by sending a command from the ODroid through the serial communication.
- As part of the temperature control feedback system one wire temperature sensors (DS10B20) are hooked up to J3.
- There are LEDs hooked to each of the stepper motor drive signals. This is designed to work in conjunction with stepper motors 28BYJ-48 5VDC. This will allow the Nano 33 BLE sense to detect their light showing that the command to move the stepper motors has been received and the motors are getting the signal to move.
- The Nano 33 BLE sense module can be read by the ODroid, through serial communications, to supply feedback that its commands have been received by this control module.
- All of the functions of the Nano 33 BLE sense, such as barometric pressure, relative humidity, spectrometer orientation, etc. can be read by the ODroid through the serial communications protocal.

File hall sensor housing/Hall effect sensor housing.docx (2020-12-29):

KY-003 Hall Effect Sensor Housing

Jerry Foote Dec 29,2020

This housing is for the KY-003 Hall Effect sensor. It is comprised of a base and lid. The .stl as well as the SolidWorks files are included.

The housing does not have provision for a cable exit as the user may have special cabling needs. An outlet for the cable can be filed on the side of the base and the cable soldered to the pads on the sensor board. The pins do not need to be removed

To assemble, place the sensor board over the pegs and press home. Apply a small amount of glue on the tops of the pegs. Route the cable out the side hole that you have filed. Place the lid on and use super glue or epoxy to hold the lid in place. Also add super glue around the cable entry for a water tight seal.

Mounting holes are provided to locate the sensor appropriately.

If you print the lid with clear or translucent material you can see the LED when the sensor is triggered.

Enjoy.

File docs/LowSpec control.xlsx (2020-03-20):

LowSpec control
 |  |  |  | LM2596 Step-Down Adjustable DC-DC Switching Buck Converter Input: 3-40VDC, Output: 1.23-37VDC 3A Price $0.99 ea 43.2mm x 21mm x 14mm
Function | Output | Input | Drive Voltage
Focus | 4 D |  | 5
Cal mirror | 4 D |  | 5
HV supply | 1 D |  | 9
Flat lamp | 1 D |  | 6-12 | Ebay High-Voltage Power Boots Step-up Module DC 6V-12V to 1000V 1500V Generator Board
Slit | 1 D |  | 5
Grating tilt | 4 D |  | 5
Heaters | 1 D |  | 12
Temp 1,2,3,4 | 1D |  | 5 or 3.3 | Dallas/Maxim 18B20
Commucations
USB
I2C
SPI
WiFi
BlueTooth
One Wire
RS232

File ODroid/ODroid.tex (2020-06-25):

\documentclass[letter,11pt,oneside]{article}

%%% (occur "\\(\\\\[a-z]*section\\|appendix\\|input\\|\\<include\\>\\)")

%%\documentclass[11pt,twocolumn]{article}
%%\usepackage[inline]{asymptote}   %% Inline asymptote diagrams
%%\usepackage{wglatex}             %% Use this one and kill others.
\usepackage{color}               %% colored letters {\color{red}{{text}}
\usepackage[listings,breakable]{tcolorbox}
\usepackage{fancyhdr}            %% headers/footers
%%\usepackage{fancyvrb}            %% headers/footers
\usepackage{datetime}            %% pick up tex date time 
\usepackage{lastpage}            %% support page of ...lastpage
\usepackage{times}               %% native times roman fonts
\usepackage{textcomp}            %% trademark
\usepackage{amssymb,amsmath}     %% greek alphabet
\usepackage{parskip}             %% blank lines between paragraphs, no indent
\usepackage{shortvrb}            %% short verb use for tables
\usepackage{lscape}              %% landscape for tables.
\usepackage{longtable}           %% permit tables to span pages wg-longtable
\usepackage{url}                 %% Make URLs uniform and links in PDFs
\usepackage{enumerate}           %% Allow letters/decorations for enumerations
\usepackage{endnotes}            %% Enhance footnotes/endnotes
\usepackage{listings}            %% Make URLs uniform and links in PDFs
\pdfadjustspacing=1                %% force LaTeX-like character spacing
%%\usepackage{geometry}            %% allow margins to be relaxed
%%\usepackage{wrapfig}             %% permit wrapping figures.
%%\usepackage{subfigure}              %% images side by side.
%%\geometry{margin=1in}            %% Allow narrower margins etc.
\usepackage[T1]{fontenc}         %% Better Verbatim Font.
\renewcommand*\ttdefault{txtt}   %% 
\usepackage[bookmarks]{hyperref} %% Make huperlinks within a PDF
%%\usepackage{natbib}   %% bibitems

%% include background image (wg-document-page-background) 

\usepackage{graphicx}            %% Include pictures into a document
%% (wg-texdoc-inserttikz)

\def\documentisdraft{NOTDRAFT}

%% (wg-texdoc-isdraft)
%% (wg-texdoc-insert-fancy-headers)

%%\usepackage[bookmarks]{hyperref} %% Make huperlinks within a PDF
%%\usepackage{makeidx}             %% Make an index uncomment following line
%%\makeindex                       %%.. yeah this one, too. index{key} in text
%%

\definecolor{verbcolor}{rgb}{0.6,0,0}
\definecolor{darkgreen}{rgb}{0,0.4,0}
\newcommand\debate[1]{\textcolor{darkgreen}{DEBATE: #1} \marginpar{\textcolor{red}{DEBATE} }}
\newcommand{\ltodo}[2]{\marginpar{\textcolor{red}{ACTION: #1}\endnote{#2}}}
\renewcommand{\thefigure}{\thesection-\arabic{figure}}
\newcommand{\menu}{\ensuremath{\;\rightarrow\;}}
\newcommand{\dhl}[1]{{\color{verbcolor}{\texttt#1}}}
\definecolor{wglightgreen}{rgb}{0.88, 0.58, 0.88}
\newcommand{\wgtextbox}[1]{\noindent\fcolorbox{darkgreen}{wglightgreen}{%
    \minipage[t]{\dimexpr0.80\linewidth-2\fboxsep-2\fboxrule\relax}
        {#1}
    \endminipage}}
%%(wg-add-inline-images)  %% add inline images to the mix
\tcbset{colback=yellow!10!white}  % tcolorbox background

%%Begin User Definitions: Hint: ~/.latex.defs and  latex.defs  
%%End User Definitions:
%%(wg-texdoc-adjust-paper-width)
%% (wg-texdoc-insert-hypersetup)

%%%%%%%%%%%%%%%%%%%%%%%%%%%%%%%%% PAGE SIZE %%%%%%%%%%%%%%%%%%%%%%%%%%%%%%%%%%%%%%%%%%%%
\pagestyle{fancy}
\usepackage[paperheight=7.125in,paperwidth=9.5in,footskip=.05in,margin=.75in,heightrounded]{geometry}
% (iv (setq tmp (/ (* 3.0 9.5) 4.0 )))   7.125
\fancyhf{}
\cfoot{{\tiny Page \thepage \hspace{1pt}}}

%%%%%%%%%%%%%%%%%%%%%%%%%%%%%%%%%%%%%%%%%%%%%%%%%%%%%%%%%%%%%%%%%%%%%%%%%%%%%

\begin{document}

%% (wg-latex-pretty-title-page)
%% (wg-texdoc-titleblock)

\title{ODroid KStars/Ekos/libindi Astronomy}
\author{Wayne Green}
\date{\today}
\maketitle

\begin{abstract}

  The ODroid OU4 is an 8-core Arm processor, here tricked out with a 64G
  eMMC card preloaded with Ubuntu 18.04. These instructions are how to
  load the ODroid to support KStars/Ekos/libindi for astronomy. It is more
  of a crib sheet. As an exercise the popular ds9 program compiled on the
  ODroid. 

\end{abstract}

%%%%%%%%%%%%%%%%%%%%%%%%%%%%%%%%%%%%%%%%%%%%%%%%%%%%%%%%%%%%%%%%%%%%%%%%%%%%%
%% table of contents
%%%%%%%%%%%%%%%%%%%%%%%%%%%%%%%%%%%%%%%%%%%%%%%%%%%%%%%%%%%%%%%%%%%%%%%%%%%%%
 
\pagenumbering{roman}   % i,ii,etc
%%\pagenumbering{gobble}   %ignore page numbers for a while
\pdfbookmark[0]{Table of Contents}{MyTOC} % if usepackage{hyperref} in use.
\tableofcontents
%%\listoffigures
%%\listoftables
\newpage

\setcounter{section}{1}
\pagenumbering{arabic}

\ifx\documentisdraft\drafttest
\linenumbers    %%%%%%%%%%%%% DRAFT
\fi

\section*{Overview}

First acquire the ODroid XU4, in my case the one with the fan. Get a
decent $\mu$SSD drive -- a Verbatim Premium 10 32G or equivalent.  I
used BalenEtcher on a Win10 to load the image.

Boot the ODroid, expand the filesystem to the whole card and bring the
image up to date.  Below are notes I took and rearranged to be in the
order of how you should do things. For example I loaded VIM (the vi
editor) early, locate\endnote{locate - Unix utility that builds a
  'database' of every file and makes searching a machine fast. When
  you add things, run \dhl{sudo updatedb} to manually rebuild the db.}
late (because it is easy to load.)  The next logical step is to get
the all the development installs done -- in this case I ran the INDI
part first.

I prefer to use ds9 as an image viewer and wanted it installed on the ODroid.
I did a \dhl{sudo apt-get install saods9} -- and the packaged program
crashs when loading a fits file iamge even though the program started up
fine. I downloaded the source, but the stock OS image was missing
quite a few libraries. One by one they were uncovered, and the
\dhl{apt-get install} lines placed to be right after the boot.
But in my actual order, I did Section \ref{sec:indipart} before
the ds9 libraries (I didn't know I needed them at that point).

I want the X11 functionalty, and I want Ekos to drop images where
I want them. I installed \dhl{NFS}, and took notes on the steps
to tie them to my main computer in Section \ref{sec:nfs}.

\subsection{Things to do once}

Using the \dhl{ssh} command, remote login to the odroid on your main
machine. You can do these things at the ODroid command prompt as well
if you like. If you are doing another odroid for the first time, then
you may have to remove its \dhl{ssh-key} -- the message will
tell you what to do:

\hskip 1cm \dhl{   ssh-keygen -f "/home/wayne/.ssh/known\_hosts" -R "odroid.local"}

Here is some code to cut/paste:

\begin{tcolorbox} %[breakable,colback=yellow!5!black]
\begingroup \fontsize{10pt}{10pt}
\selectfont
\begin{verbatim} 
# If this is a different odroid might have to remove the
# old hash from the .ssh/known_hosts file.
#ssh-keygen -f "/home/wayne/.ssh/known_hosts" -R "odroid.local"
ssh -l odroid odroid.local  # see remove old key above

# fix up the ~/.bashrc to git rid of colors. (hard to see)
echo "export PS1='(\j) \h \w [\!] '" >> ~/.bashrc
echo "alias ls='ls -FC'"            >> ~/.bashrc
echo "
\end{verbatim}
\endgroup
\end{tcolorbox}

\subsection{Initialize for KStars}

Here we remote login via ssh into the odroid, and follow
the commands below. It may require a reboot or two.
This is for a first time load. A short cut for the
huge KStars libraries and some default stuff you may
want will be developed below. (\today)

\begin{tcolorbox} %[breakable,colback=yellow!5!black]
\begingroup \fontsize{10pt}{10pt}
\selectfont
\begin{verbatim} 
#Setup
ssh -l odroid odroid.local  # see remove old key above

sudo apt-get update
sudo apt-get upgrade              # N - keep the provider's /etc/apt-fast.conf
sudo apt-get dist-upgrade
sudo apt-get install -y vim       # because,,, vi!
sudo apt install -y git           # because,,, git! (astrometry.net)

# Load these packages now, get it over with for ds9.
# Handy anyway.
sudo apt-get install -y locate       # bacause,,, locate!
sudo apt-get install -y libx11-dev   # needed for ds9
sudo apt-get install -y zlib1g-dev   # needed for ds9
sudo apt-get install -y libxml2-dev  # needed for ds9
sudo apt-get install -y libxslt1-dev # needed for ds9
sudo apt-get install -y autoconf     # needed for ds9

# for astrometry.net
sudo apt-get install -y swig
sudo apt-get install -y  python3-dev python3-pip python3-virtualenv
\end{verbatim}
\endgroup
\end{tcolorbox}

\subsection{KStars/EkosINDI part}  \label{sec:indipart}

Load the packages, and then using the KStars interface initialize the
site location etc, and load the internal things like lots of Tycho
stars. Add the Atik support libraries.

\begin{tcolorbox} %[breakable,colback=yellow!5!black]
\begingroup \fontsize{10pt}{10pt}
\selectfont
\begin{verbatim} 
# Indi/KStars
sudo apt-add-repository -y ppa:mutlaqja/ppa
sudo apt-get update
sudo apt-get install indi-full
sudo apt-get install kstars-bleeding

Atik Cameras:
sudo add-apt-repository -y ppa:mutlaqja/ppa
sudo apt-get update
sudo apt-get install indi-atik
sudo apt-get install libindi1     # moonlite NiteCrawler focuser

\end{verbatim}
\endgroup
\end{tcolorbox}

\subsection{Remote X Desktop}  \label{sec:xrdp}

This part will be idle most of the time -- but still cycle-sucking.
I did it anyway.

\begin{tcolorbox} %[breakable,colback=yellow!5!black]
\begingroup \fontsize{10pt}{10pt}
\selectfont
\begin{verbatim} 
# https://linuxize.com/post/how-to-install-xrdp-on-ubuntu-18-04/
apt install xfce4 xfce4-goodies xorg dbus-x11 x11-xserver-utils
apt install xrdp 

systemctl status xrdp
adduser xrdp ssl-cert  
systemctl restart xrdp
ufw allow from 192.168.1.0/24 to any port 3389
ufw allow 3389
\end{verbatim}
\endgroup
\end{tcolorbox}

\subsection{SAOImage/ds9}  \label{sec:ds9}

Odroid:

\begin{tcolorbox} %[breakable,colback=yellow!5!black]
\begingroup \fontsize{10pt}{10pt}
\selectfont
\begin{verbatim} 
cd /Downloads
wget http://ds9.si.edu/download/source/ds9.8.1.tar.gz
tar xzvf ds9.8.1.tar.gz  # -> makes SAO
cd SAO
make unix/install > log0 2>&1
make >> log0 2>&1
tail -f log0  # ties the window up watching the make
\end{verbatim}
\endgroup
\end{tcolorbox}

This went on for quite a while, each failure ment tracking
down the missing library, adding that to the top of
this file, and going again. It was painful, fortunately
I knew ds9 when it was sane, and could decipher the
twisted package names.

Eventually:

\begin{tcolorbox} %[breakable,colback=yellow!5!black]
\begingroup \fontsize{10pt}{10pt}
\selectfont
\begin{verbatim} 
ssh -X odroid@odroid # from titan
ds9 theOdroidFits.fits # pops up an X display on Titan!
\end{verbatim}
\endgroup
\end{tcolorbox}
But, downloads bog down the ODroid, so we want INDI to
drop the file via the network onto \dhl{titan}! So
on to NFS.

\subsection{ODroid in the Network}  \label{sec:networking}

In this example, my main machine \dhl{titan} lives on
my network at \dhl{192.168.0.216}. Currently the ODroid
uses DHCP and is at \dhl{192.168.0.218} -- I maintain
long DHCP leases with renewal on my network host.

The ODroid is gig-Ether.

I added \dhl{192.168.0.216} to the odroid \dhl{/etc/hosts} file.
I added \dhl{192.168.0.218}  to titans \dhl{/etc/hosts} file.

Titan has the nfs-server installed, has been for years.

Titan has one-and-only one file that matters: the \dhl{/etc/exports}
file. It needs one line added to allow the ODroid to come in
as a user.

The ODroid needs to have the \dhl{nfs-common} package installed,
one line added to its /etc/fstab, and a little helper script
added to \dhl{/etc/network/if-up.d/fstab} to mount the nfs
connection during odroid-boot. (I suspect late rc2, before rc3).
I don't care, I want it ready with run-level 5 hits.

\subsection{NFS}  \label{sec:nfs}

Third things first: This machine is behind at least 3 routers
in my system, the last is the WAN gateway.

Getting NFS was a bit painful to implement and I need to dig into
some security issues. I should do the export on titan
ONLY for ODroid's IP address for example. It's been 30 years
since I had to do this for a living.

Firewalls need to be explored and opened. My IPtables are a bit goofy
on titan as it does Strange Things\texttrademark\; with Docker
containers, and the rest of my network.

When the camera takes an image, it will put the image into
\dhl{ordoid:/mnt/titantoday} that winds up on
\dhl{titan:/export/wayne/titantoday}. So, AS the camera
is downloading -- the network is churning and the file's write
finishes on \dhl{titan}. While the next hammering download
is taking place, titan does not feel the impact so much.

Note: This will have to change for high cadence work,
but it is not too bad.

NFS is a Unix/Unix network file sharing program. I trust it more than
SMB -- but SMB has made progress. It is the one I choose, as my
analysis routines are Unix based on a remote server anyway.

I suspect a NFS/Tunneling might be slower.

Or, I may implement a ``pull'' strategy from titan, to
get the files over when I want them. This means titan will
not see the camera download at all.

\begin{tcolorbox}[breakable]
\begingroup \fontsize{10pt}{10pt}
\selectfont
%%\begin{Verbatim} [commandchars=\\\{\}]
\begin{verbatim} 
# Now to get NFS working
#On odroid
# safer? sudo ufw allow from 192.168.0.216/32 to any port nfs
sudo ufw allow from 192.168.0.0/24 to any port nfs
sudo ufw status
sudo apt install nfs-common
---------------------------------
# odroid /etc/fstab
UUID=e139ce78-9841-40fe-8823-96a304a09859 / ext4 errors=remount-ro,noatime 0 1
LABEL=boot /media/boot vfat defaults 0 1
titan:/export/wayne/ /mnt/titantoday nfs rw,async,user,auto 0 0 

mount -a
# manual way... mount titan:/export/wayne/ /mnt/titantoday/

# add a config script to mount fs
cat >/etc/network/if-up.d/fstab
#!/bin/sh
mount -a
^D
chmod +x /etc/network/if-up.d/fstab
---

#On titan: edit /etc/exports
/export       192.168.0.1/24(rw,fsid=0,insecure,no_subtree_check,async)
/export/users 192.168.0.0/24(rw,nohide,insecure,no_subtree_check,async)
/export/wayne 192.168.0.0/24(rw,async,no_subtree_check,anonuid=1000,anongid=1000)
sudo exportfs -av

# I suspect the line CIDR /32 = netmask of 255.255.255.255 or precise macine.
# anonuid=1000,anongid=1000 is a bit concerning! It requires agreement in
# user's ids between machines and 1000 is default linux install.
/export/wayne 192.168.0.216/32(rw,async,no_subtree_check,anonuid=1000,anongid=1000)

\end{verbatim}
\endgroup
%% \end{Verbatim}
\end{tcolorbox}
\section{Summary/Things to do}

Three-D print a case that will hold on to something. Probably
my Alpy-600 to start. That fan is a bit questionable, but another
is hammering away at the back of the camera.

I still need to write the task that drives ds9 when new images
shows up. Did a lot of documentation on that as I was trying
to get that to work from inside a Docker container. Futile
I suspect, but I am sure learning networking on Docker's virtual
net.

\section{Operations}

It is possible to store images both 'locally' on the ODroid,
and remotely (see NFS above.)

the \dhl{\~/Desktop/Today} is where all the software
has been configured (in the past!) to use. At the
end of the night, Rename this and copy to local
machine as needed.

With NFS, the copies are done one-by-one in realtime.

\begin{tcolorbox} %[breakable,colback=yellow!5!black]
\begingroup \fontsize{10pt}{10pt}
\selectfont
%%\begin{Verbatim} [commandchars=\\\{\}]
\begin{verbatim} 
ssh -l odroid@odroid.local
...pw...

cd Desktop

ls -l Today          # see if exists,
mv Today when.Today  # move it to the 'right' date
mkdir Today          # make todays.
\end{verbatim}
\endgroup
%% \end{Verbatim}
\end{tcolorbox}

\section{Use with The Sky/X (TSX)} \label{sec:skyx}

The remote use requires the TCP/IP address of the
mount controler. TSK \dhl{Tools->TCP Server}, the port is
\dhl{3040} by default. On the same computer, set the
TCP/IP address to localhost \dhl{127.0.0.1}.

\url{https://www.indilib.org/devices/mounts/bisque-paramount.html}

\index{TSX!port} \index{TSK!TCP/IP}

\section{Astrometry.net Local}  \label{sec:astrommetry}

The main documentation is at: \index{AstrometryNet!Documentation}

\url{http://astrometry.net/doc/index.html}

The \dhl{Astrometry.net} package can be obtained via git.
\index{AstrometryNet!Build Instructions}

\begin{tcolorbox} %[breakable,colback=yellow!5!black]
\begingroup \fontsize{10pt}{10pt}
\selectfont
%%\begin{Verbatim} [commandchars=\\\{\}]
\begin{verbatim} 
mkdir -p ~/git/{clones,external}
mkdir -p ~/clones
cd ~/clones
wget http://heasarc.gsfc.nasa.gov/FTP/software/fitsio/c/cfitsio-3.48.tar.gz
tar xzvf cfitsio-3.48.tar.gz
cd cfitsio-3.48
./configure
make > log1 2>&1 &
tail -f log1
view Makefile # make sure install dir is right. Ha! prefix=/usr needed
sudo make prefix=/usr install

#git clone ....the clone from github
cd ~/git/external
git clone https://github.com/dstndstn/astrometry.net.git
cd astrometry.net
# in the background, run make and watch for errors with tail -f
make > log1 2>&1 &
tail -f log1
# ... take a minute! ...
# making this documentation, cfitsio was missing, see above
make > log2 2>&1 &
tail -f log2
# OK had to pause and install swig (above)
make > log3 2>&1 &
tail -f log3

# OK had to pause and install python dev (above)
make > log4 2>&1 &
tail -f log4

sudo make install INSTALL_DIR=/usr/local >install.log 2>&1
less install.log

# get some index files
# first-off download them to a local place on your
# network, then copy them here to the ODroid.
# get wayne's handy scripts.
\end{verbatim}
\endgroup
%% \end{Verbatim}
\end{tcolorbox}

\subsection{Index Files}

The pagkage is installed at a given root location, here
\dhl{/usr/local/share/astrometry}. The
data files are controled by a file called \dhl{etc/astrometry.cfg}.

\begin{tcolorbox} %[breakable,colback=yellow!5!black]
\begingroup \fontsize{10pt}{10pt}
\selectfont
%%\begin{Verbatim} [commandchars=\\\{\}]
\begin{verbatim} 
add_path /usr/local/astrometry/data
autoindex
\end{verbatim}
\endgroup
%% \end{Verbatim}
\end{tcolorbox}

The two lines use all the files in the \dhl{/usr/local/astrometry/data}
location. There are three strategies:

- Keep all the files together in the \dhl{data} directory.

Acquire the INDEX-42 files.

\begin{table}[h!]
%\phantomsection
%\addcontentsline{toc}{section}{ TOC CAPTION}
% \setlength{\belowcaptionskip}{6pt} % adjust space under caption abovecaptionskip
% \renewcommand{\arraystretch}{1.3} % adjust line spacing
%\small{
%\begin{minipage}{\textwidth}     % for footnotes in table.
%\caption[TOC]{Index File Scales}
\centering
\begin{tabular}{| l | l | r  r | r  r |}
%\MakeShortVerb{\|}
%\multicolumn{n}{fmt}{text for merged cols}
\hline
Scale &  File                 & \multicolumn{2}{| l |}{  Range}    &  \multicolumn{2}{| l |}{ Range }  \\
      &                       & \multicolumn{2}{| l |}{  (arcmin)} & \multicolumn{2}{| l |}{ (degrees) } \\
\hline
00    &  index-4200-*.fits    &     2.0  &    2.8 &           &    \\    
01    &  index-4201-*.fits    &     2.8  &    4.0 &           &    \\ 
02    &  index-4202-*.fits    &     4.0  &    5.6 &           &    \\ 
03    &  index-4203-*.fits    &     5.6  &    8.0 &           &    \\ 
\hline
04    &  index-4204-*.fits    &     8    &    11  &           &    \\ 
05    &  index-4205-*.fits    &     11   &    16  &           &    \\ 
06    &  index-4206-*.fits    &     16   &    22  &           &    \\ 
07    &  index-4207-*.fits    &     22   &    30  &           &    \\ 
08    &  index-4208.fits      &     30   &    42  &           &    \\ 
09    &  index-4209.fits      &     42   &    60  &           &    \\ 
10    &  index-4210.fits      &     60   &    85  &           &    \\ 
11    &  index-4211.fits      &     85   &   120  &      1.42 &   2.00    \\ 
\hline
12    &  index-4212.fits      &     120  &   170  &      2.00 &   2.83    \\ 
13    &  index-4213.fits      &     170  &   240  &      2.83 &   4.00    \\ 
14    &  index-4214.fits      &     240  &   340  &      4.00 &   5.67    \\ 
15    &  index-4215.fits      &     340  &   480  &      5.67 &   8.00    \\ 
16    &  index-4216.fits      &     480  &   680  &      8.00 &  11.33    \\ 
17    &  index-4217.fits      &     680  &  1000  &     11.33 &  16.67    \\ 
\hline
18    &  index-4218.fits      &     1000 &  1400  &     16.67 &  23.33    \\ 
19    &  index-4219.fits      &     1400 &  2000  &     23.33 &  33.33    \\ 
%% ones-based: \cline{a-b}
\hline
%%\DeleteShortVerb{|}
\end{tabular}
%%\end{minipage}    %% for footnotes  r@{.}l 
\caption[TOC]{Index File Scales}
\label{table:IndexFileScales}
%%} % end small etc
\end{table}

Make GAIA index files.
\url{https://github.com/LCOGT/gaia-astrometry-net}

Get Pre-made GAIA files for scales 00 through 07. 194 files.
\url{http://data.astrometry.net/5000/}

\section{Summary} \label{sec:summary}

The KStars planetarium packages leaves quite a bit to be desired,
but allows one to add their own libraries, and control cameras etc.
The ODroid/KStars/Ekos/INDI suite, with configuration tricks here
allows the odroid to happily live on the telescope without
keyboard/mouse/monitor. IT requires power and Ethernet from the
outside -- and connections to the instrument: USB for the camera
and perhaps USB for the filter wheel.

%%\appendix
%%\renewcommand \thesection{\Alph{section}}

%% use a bibitem approach to the references publications etc.
%% (wg-bibitem)

%%\clearpage
%%\addcontentsline{toc}{section}{References}
%%\renewcommand*{\refname}{My Bibliography and References}
%%\bibliographystyle{plain}	% bibliographystyle{apalike} and \usepackage{natbib}
%%\bibliography{MasterBib}	% expects file "MasterBib.bib"

%%\clearpage
%%\addcontentsline{toc}{section}{Index}
%%\printindex %% www.cs.usask.ca/resources/tutorials/latex/notes/toc-index.pdf

%%\begin{thebibliography}{80}
%%\usepackage{natbib}   %% bibitems
%%\end{thebibliography}

% /home/wayne/git/pre/pre.Odroid/doc/Odroid.tex

%% (wg-texdoc-endnotes)
\end{document}

#on odroid
# add titan to /etc/hosts
echo "192.168.0.216 titan" >> /etc/hosts

# add export info on titan/restart nfs
/export/wayne 192.168.0.0/24(rw,async,no_wdelay,no_root_squash,insecure_locks,sec=sys,anonuid=1025,anongid=100)
systemctl restart nfs-kernel-server

#Add to tail of /etc/fstab
titan:/export/wayne/Today /home/odroid/desktop/Today nfs rw,user,auto 0 0

---
https://linuxconfig.org/how-to-configure-a-nfs-file-server-on-ubuntu-18-04-bionic-beaver

#titan /etc/exports
/export       192.168.0.1/24(rw,fsid=0,insecure,no_subtree_check,async)
/export/users 192.168.0.0/24(rw,nohide,insecure,no_subtree_check,async)
#/export/wayne 192.168.0.0/24(rw,nohide,insecure,no_subtree_check,async)
/export/wayne 192.168.0.0/24(rw,async,no_wdelay,no_root_squash,insecure_locks,sec=sys,anonuid=1025,anongid=100)

Kevin AVX mount.

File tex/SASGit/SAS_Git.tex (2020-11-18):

\documentclass[letter,11pt,oneside]{article}
%%% HEREHEREHERE
%%% APPENDIX
%%% (insert (format "\n%s\n" (buffer-file-name)))
%%% (occur "\\(\\\\[a-z]*section\\|appendix\\|input\\|\\<include\\>\\)")

%%\documentclass[11pt,twocolumn]{article}
%%\usepackage[inline]{asymptote}       %% Inline asymptote diagrams
%%\usepackage{wglatex}                 %% Use this one and kill others.
\usepackage{color}                     %% colored letters {\color{red}{{text}}
\usepackage[listings,breakable]{tcolorbox}
\usepackage{fancyhdr}                  %% headers/footers
\usepackage{fancyvrb}                %% headers/footers
\usepackage{datetime}                  %% pick up tex date time
\usepackage{lastpage}                  %% support page of ...lastpage
\usepackage{times}                     %% native times roman fonts
\usepackage{textcomp}                  %% trademark
\usepackage{amssymb,amsmath}           %% greek alphabet
\usepackage{parskip}                   %% blank lines between paragraphs, no indent
\usepackage{shortvrb}                  %% short verb use for tables
\usepackage{lscape}                    %% landscape for tables.
\usepackage{longtable}                 %% permit tables to span pages wg-longtable
\usepackage{multicol}                  %% Enhance footnotes/endnotes
\usepackage{url}                       %% Make URLs uniform and links in PDFs
\usepackage{enumerate}                 %% Allow letters/decorations for enumerations
\usepackage{endnotes}                  %% Enhance footnotes/endnotes
\usepackage{listings}                  %% Make URLs uniform and links in PDFs
\pdfadjustspacing=1                    %% force LaTeX-like character spacing
%%\usepackage{geometry}                  %% allow margins to be relaxed
%%\usepackage{wrapfig}                 %% permit wrapping figures.
%%\usepackage{subfigure}               %% images side by side.
%%\geometry{margin=1in}                  %% Allow narrower margins etc.
\usepackage[T1]{fontenc}               %% Better Verbatim Font.
\renewcommand*\ttdefault{txtt}        %%
\usepackage[bookmarks,colorlinks=true]{hyperref} %% Make huperlinks within a PDF
\usepackage{natbib}                    %% bibitems

%% include background image (wg-document-page-background)

\usepackage{graphicx}            %% Include pictures into a document
%% (wg-texdoc-inserttikz)

\def\documentisdraft{NOTDRAFT}

%% (wg-texdoc-isdraft)
%% (wg-texdoc-insert-fancy-headers)

%%\usepackage[bookmarks]{hyperref} %% Make huperlinks within a PDF
%%\usepackage{makeidx}             %% Make an index uncomment following line
%%\makeindex                       %%.. yeah this one, too. index{key} in text
%%

\definecolor{verbcolor}{rgb}{0.6,0,0}
\definecolor{darkgreen}{rgb}{0,0.4,0}
\newcommand\debate[1]{\textcolor{darkgreen}{DEBATE: #1} \marginpar{\textcolor{red}{DEBATE} }}
\newcommand{\ltodo}[2]{\marginpar{\textcolor{red}{ACTION: #1}\endnote{#2}}}
\renewcommand{\thefigure}{\thesection-\arabic{figure}}
\newcommand{\menu}{\ensuremath{\;\rightarrow\;}}
\newcommand{\dhl}[1]{{\color{verbcolor}{\texttt#1}}}
\definecolor{wglightgreen}{rgb}{0.88, 0.58, 0.88}
\newcommand{\wgtextbox}[1]{\noindent\fcolorbox{darkgreen}{wglightgreen}{%
    \minipage[t]{\dimexpr0.80\linewidth-2\fboxsep-2\fboxrule\relax}
        {#1}
    \endminipage}}

\newcommand\snippet[2]{%
\begin{figure}[h!]
\begin{tcolorbox}[colback=yellow!15!white]
\begingroup \fontsize{10pt}{10pt}
\selectfont
\VerbatimInput{snippets/#1}
\endgroup
\end{tcolorbox}
\caption{#2}
\label{fig:KStarsPreliminary}
\end{figure}
}

\hypersetup{
colorlinks=true,
linkcolor=red,
citecolor=red,
urlcolor=blue,
pdfauthor = {Copyright(c) 2020. All rights reserved. Wayne Green},
pdftitle = {Astro Docker: Sextractor and Astrometry.net},
pdfsubject = {Photometry Reduction},
pdfkeywords = {photometry, astrometry},
pdfcreator = {LaTeX with hyperref package},
pdfproducer = {dvips + ps2pdf}}

%%(wg-add-inline-images)  %% add inline images to the mix

%%%%%%%%%%%%%%%%%%%%%%%%%%%%%%%%% PAGE SIZE %%%%%%%%%%%%%%%%%%%%%%%%%%%%%%%%%%%%%%%%%%%%
\pagestyle{fancy}
\usepackage[paperheight=7.125in,paperwidth=9.5in,footskip=.05in,margin=.75in,heightrounded]{geometry}
% (iv (setq tmp (/ (* 3.0 9.5) 4.0 )))   7.125
\fancyhf{}

%%%%%%%%%%%%%%%%%%%%%%%%%%%%%%%%%%%%%%%%%%%%%%%%%%%%%%%%%%%%%%%%%%%%%%%%%%%%%

\begin{document}

%% (wg-latex-pretty-title-page)

%%%%%%%%%%%%%%%%%%%%%%%%%%%%%%%%%%%%%%%%%%%%%%%%%%%%%%%%%%%%%%%%%%%%%%%%%%%%%
%%%%%%%%%%%%%%%%%%%%%%%%%%%% START PRETTY TITLE PAGE %%%%%%%%%%%%%%%%%%%%%%%%%%%%%%%%%
\pagecolor{blue!50}

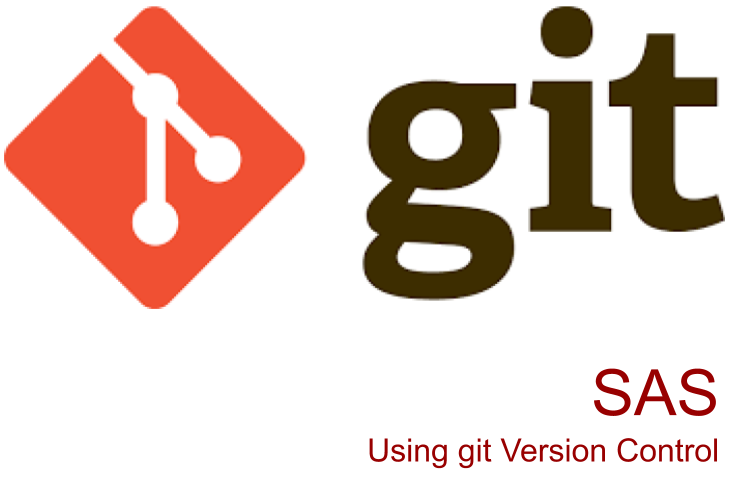
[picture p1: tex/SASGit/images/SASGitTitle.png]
 \\
\vskip 1mm {\tiny git consortium}

\pagenumbering{gobble}   %ignore page numbers for a while

\newpage
\pagecolor{white}

%% (wg-texdoc-titleblock)

\setcounter{section}{0}
\pagenumbering{arabic}

\ifx\documentisdraft\drafttest
\linenumbers    %%%%%%%%%%%%% DRAFT
\fi

\newpage

\section*{Overview}

We use ``git'' to keep versions of images in a central ``cloud'' location.

Developers new to the project ``clone'' this image in its entirty.

It is possible to get just the recent images related to the project.

You make your local copy and do some work.
\vspace{-.15cm}
\begin{enumerate}\addtolength{\itemsep}{-0.5\baselineskip}
   \item   New files
   \item   Modify existing files
\end{enumerate}

Several modifications, until you are ready to ``add'' those changes
back into the mainstream. 

Then you ``commit'' to the files you added, adding a brief message
about what was done. This updates your local copy.

Then you ``push'' your changes to the remote location to be available
for all.

So:

\vspace{-.15cm}
\begin{enumerate}\addtolength{\itemsep}{-0.5\baselineskip}
   \item   Clone - make a copy of a repository, that is a repository in its own
             right.
   \item   Work - Do work in the directory with an eye to permenant changes.
   \item   Add  - Add the new/updated to the local list of things to make
            permenant in the local repository.
   \item   Commit - Commit those changes locally.
   \item   Push - Push the changes out to the rest of the world. Its on you
           to make sure you don't break anything.
   \item   Pull - Get other peoples changes down to the local level.
\end{enumerate}

With git, the main development ``thread'' is called the ``master
branch''\footnote{The current repository is called ``master'', the new move
is to call the main branch, well ``main''.} and is usually the stable 
path for the code. When new ideas are agreed upon, you create a ``branch'',
do the work/add/commit (locally) -- until you are happy. You may push
those changes up to the remote repository's ``branch'' of the same name --
issue a pull requiest; have your peers work on the code with changes etc.
At some point, the results of the branch are ``merged'' back into the ``main
branch'' and a ``release'' is made. This ``release'' is ``tagged'' with
a revision number, and life moves on.

Branches may be branched even deeper. This may allow two competing ideas
to duke it out -- surviver is merged upward.

Rinse and Repeat.

\subsection{Bits of Arcana}

\subsection{Issues}

We maintain ``private'' repositories:
\vspace{-.15cm}
\begin{enumerate}\addtolength{\itemsep}{-0.5\baselineskip}
   \item   Respect the priviledge of everyone's privacy
   \item   Yours is respected to the extent possible (hackers are good)
   \item   We will all agree to make the repository public, or not.
\end{enumerate}

Here we try to distill the capabilities of a program to meet a complex
issue of managing changes for projects in a way as to be 100\% safe
in retaining code, documentation, and data.

\newpage

\section{Get Started}

It is critical to have an agreed-upon way to put information into
a version control system. This respects other people's ability to
find things.

To join the SAS Spectrography GitHUB project:

\vspace{-.15cm}
\begin{enumerate}\addtolength{\itemsep}{-0.5\baselineskip}
   \item   Go to \url{https://github.com/}
   \item   Sign-up (please fill in the damned profile and provide a recognizable icon).
   \item   Send login name to project leader
\end{enumerate}

The project leader will add you to the list of people that use the
reposirory.

\section{GIT Version Control}

The ``git'' package was written in over several weeks, yes weeks,
because Linux Torvalds was disappointed with existing ``version
control'' systems. It went through a brief period of improvement
by the team that manages the roughtly 1e6 lines of the Linux Kernel.
It was released, and in minor ways, improved over the years.

Git forms the foundation for almost all serious code develoment.
It is not limited to code. 

The basic idea, is each file is copied to a ``main'' repository ``somewhere''.
The files are saved with a name that ``is'' the SHA1 hash code for
their contents -- offering a one in 1e48-ish chance of two different
files having the same name. A little side-table tracks the file's real
name. 

In a repository, such as the one on GitHub, has copies of each revision
of the file -- going back. 

You can make a complete copy of that repository onto your machine. That
repository is just as capable of being the main repo -- main by virtue
of being agreed-upon by social convention. 

A truly independent mirroring of important details that makes it
almost impossible\footnote{Barring stupidity that is in abundant
  supply.} for a ``bad actor'' to create Chaos\texttrademark.

\appendix
\renewcommand \thesection{\Alph{section}}

\section{Examples}

\subsection{Use the Browser to Add New Files}

Go to the GitHub repository and log in.

To create a new directory, the fast way, is to create a new file
MyNewDirName/README.md -- to start a README file (good idea anyway)
and put in some descriptive information about this thing.

Then simply browse down into the new directory, drag and drop
the new files ``up there''.

\section{Under the Hood}

%% use a bibitem approach to the references publications etc.
%% (wg-bibitem)

%%\clearpage
\addcontentsline{toc}{section}{References}
\renewcommand*{\refname}{My Bibliography and References}
\bibliographystyle{apalike}	% bibliographystyle{apalike} and \usepackage{natbib}
\bibliography{MasterBib}	% expects file "MasterBib.bib"

%%\begin{thebibliography}{80}
%%\usepackage{natbib}   %% bibitems
%%\end{thebibliography}

%%\clearpage
%%\addcontentsline{toc}{section}{Index}
%%\printindex %% www.cs.usask.ca/resources/tutorials/latex/notes/toc-index.pdf

% /home/wayne/iraf/smtsci/tex/SextractorDocker.tex

%% (wg-texdoc-endnotes)

%%%%%%%%%%%%%%%%%%%%%%%%%%%%%%%%%%%%%%%%%%%%%%%%%%%%%%%%%%%%%%%%%%%%%%%%%%%%%
% Support for endnotes
\begingroup
\renewcommand{\notesname}{\textcolor{red} {Action Items:}}
\parindent 0pt
\parskip 2ex
\phantomsection
\addcontentsline{toc}{section}{	extcolor{red} {Action Items:}}
\def\enotesize{\normalsize}
\theendnotes
\endgroup

\end{document}

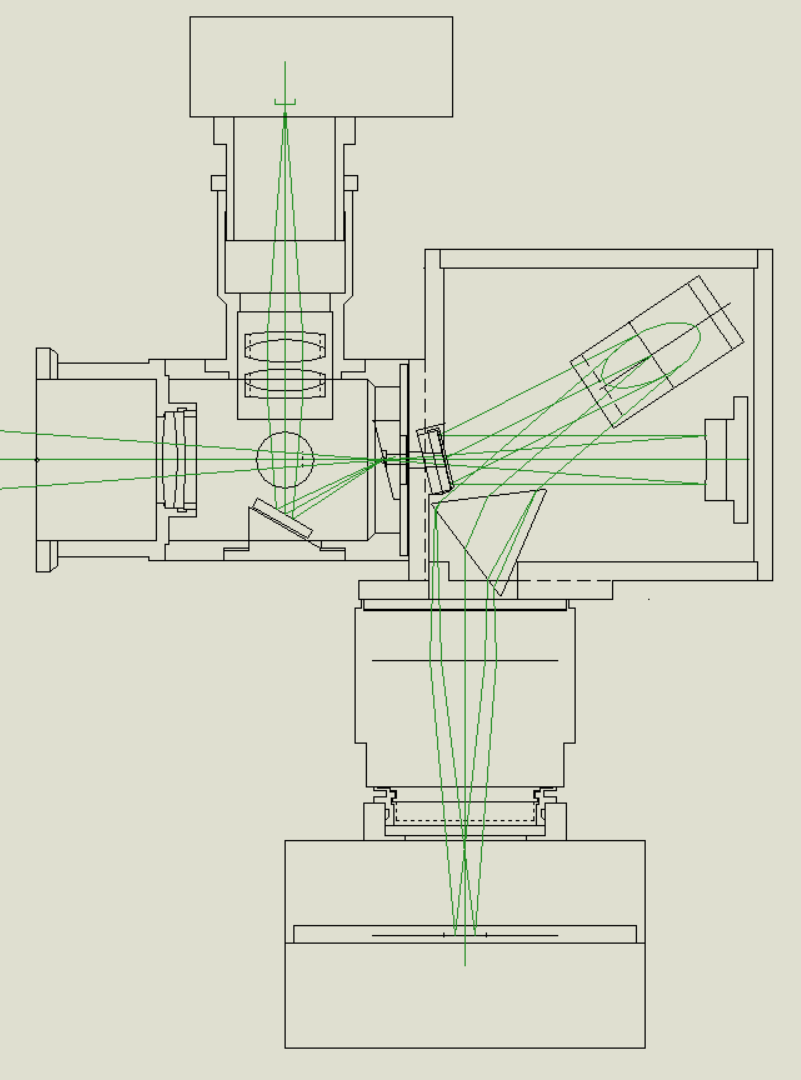
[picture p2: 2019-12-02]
Eschelle/EchelleOpticalPath.PNG

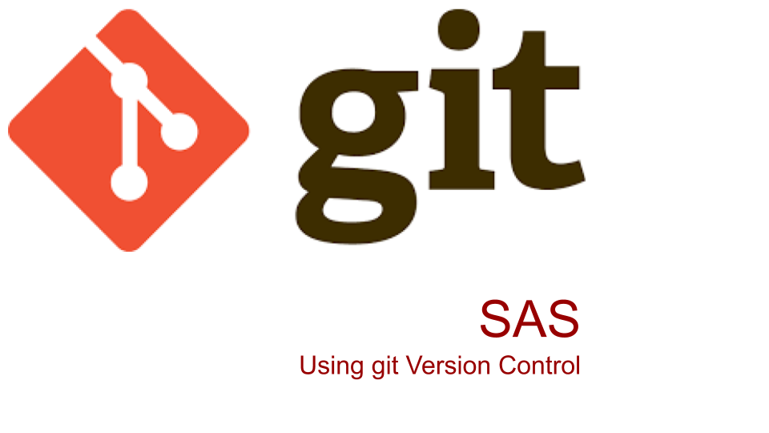
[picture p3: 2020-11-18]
tex/SASGit/images/SASGit.png

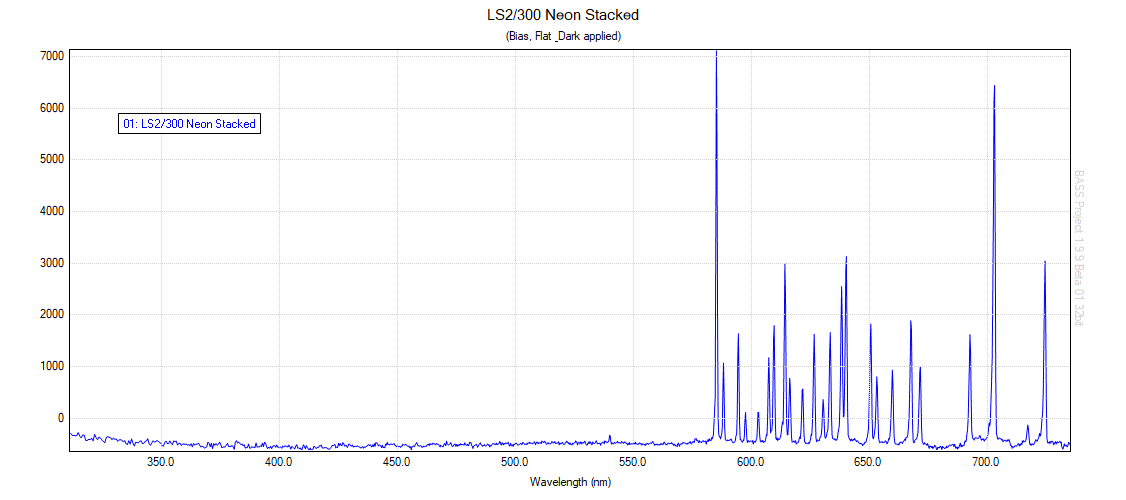
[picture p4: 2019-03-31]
docs/TuningLOWSPEC2_Tuning/images/Figure1.png

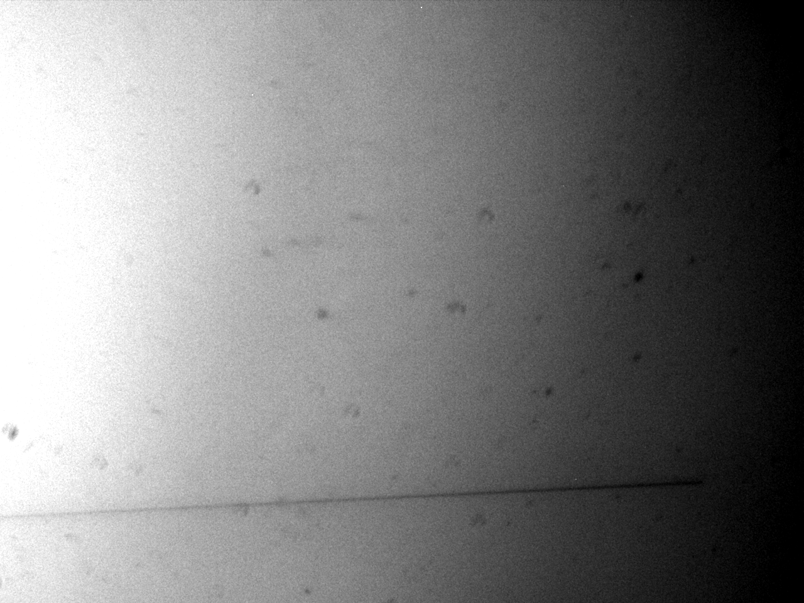
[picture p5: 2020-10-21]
TonyLowspec2/32mmT4Ovio30um.tif

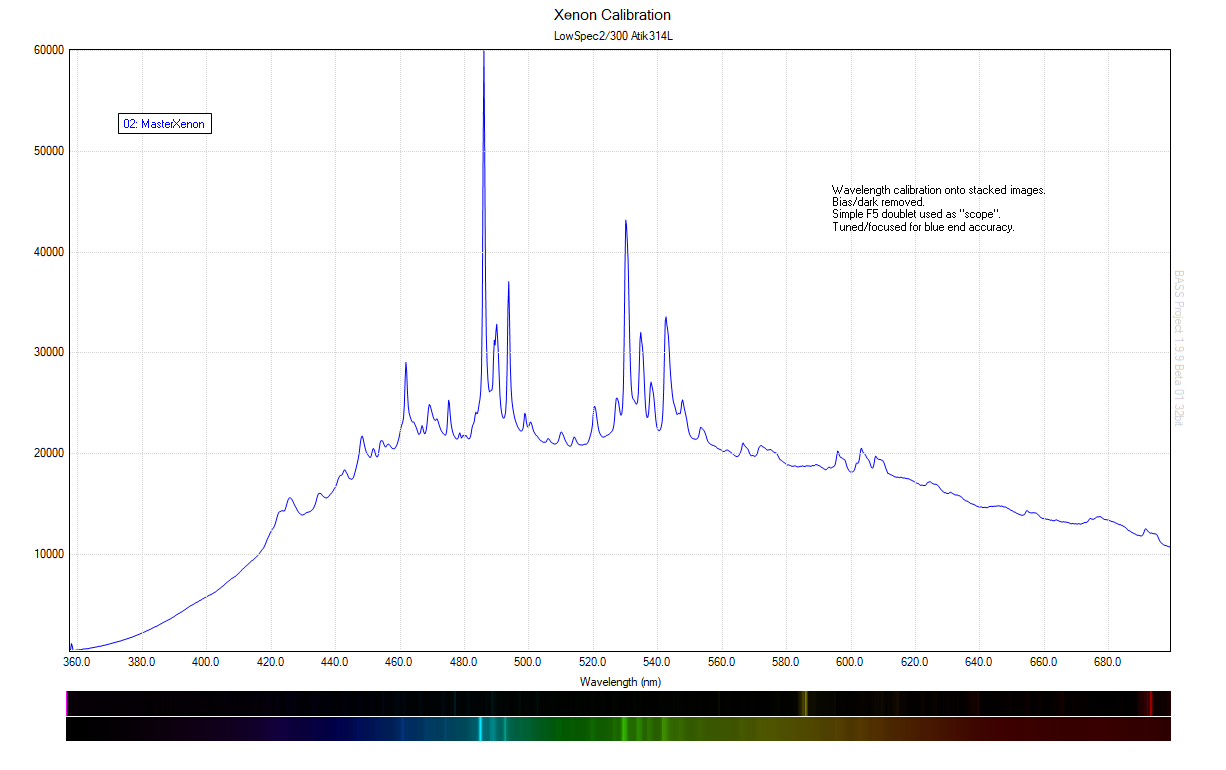
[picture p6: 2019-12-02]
TonyLowspec2/Xenon.png

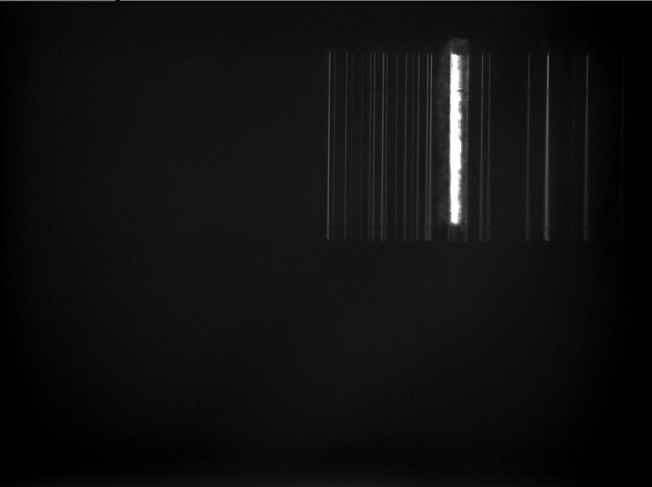
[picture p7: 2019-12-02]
TonyLowspec2/LS2300SXNeonRedPen2.jpg

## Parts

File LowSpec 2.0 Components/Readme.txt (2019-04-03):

Information regarding the components required to print and operate the LowSpec spectrograph

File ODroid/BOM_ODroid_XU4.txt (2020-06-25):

ODroid XU4 with Fan. You also want to get the emmc card with linux,
a power supply, and the emmc reader/writer to backup etc.

The rest is a pdf that I have put together.

https://www.hardkernel.com/shop/odroid-xu4-special-price/
https://www.hardkernel.com/shop/64gb-emmc-module-xu4-linux/
https://www.hardkernel.com/shop/5v-4a-power-supply-us-plug-2/
https://www.hardkernel.com/shop/usb3-0-emmc-module-writer/

Probably better to print a box, not happy with the one I bought.

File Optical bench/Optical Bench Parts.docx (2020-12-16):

Optical Bench Parts

Jerry Foote 11/19/2020

Basic idea for the system is to have a Standard Base of specific size (20mm W x 40mm L x 10mm H), with provision for 3 N52 magnets imbedded in the base, a standard opening in the top for mounting specific components with a locking screw to hold the component in place and a side groove that allows the use of an alignment rod/angle/square to align multiple bases. In use multiple Standard Bases, with there attached components, are placed on a steel plate at the appropriate locations for the design. The steel plate can be made from a flat Melamine shelf with a galvanized steel sheeting contact cemented to its top providing a flat working magnetic surface.

By design the optical axis is located at 50mm above the surface. Ten mm of this is the Standard Base height. The difference in height between the Standard Base and the optical axis of 40mm is to allow a wide variety of components to be used.

Standard Base

The magnets for the base are N52 10mm in diameter and 2mm thick. The holes have been made slightly deeper so that the base bottom is the height reference. The magnets are super glued into the base. The locking screw is a M3-.05 x 10mm which engages a M3-0.5 nut pressed into the slot in the base top.

The standard opening in the base for component mounting is 14mm x 6mm x 7mm deep. The mating component part should have shoulders such that the mating component does NOT bottom out in the opening rather sits on the top of the Standard Base.

Representative 30mm lens component holder

This is a holder for a 30mm lens and shows how the mating component might work.

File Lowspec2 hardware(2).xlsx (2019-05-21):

LowSPEC Mark 2 |  | 2019-05-20 | Foote | https://www.thingiverse.com/thing:2455390
Ordered | Part | QTY | Qty (where used) | Vendor | Catalog # | Qrt @ | Price | Notes
1 | Socket head cap screw M4 x 60mm | 5 | 5 (38) | McMaster-Carr | 91292A048 | 25 | $6.54
1 | M4 Lock nut | 5 | 5 (20) | McMaster-Carr | 93625A150 | 100 | $6.04
1 | M5 Lock nut | 2 | 12(9) | McMaster-Carr | 91831A411 | 100 | $6.27
1 | M3 nut | 9 | 4 (6)+1(11)+1(14)+2(20)+1(29) | McMaster-Carr | 91828A211 | 100 | $5.55
1 | Allen set screw flat top m4 x 0.7 x 10mm | 8 | 4(2)+1(5)+3(15) | McMaster-Carr | 93245A114 | 100 | $12.30
1 | Allen set screw flat top end M4 x 0.7 x 6mm | 4 | 2(2)+2(34) | McMaster-Carr | 93245A112 | 100 | $9.95
1 | M3 x 25mm philips flat head | 1 | 1 (15) | McMaster-Carr | 92125A138 | 100 | $11.50 | Hex Drive
1 | M3 x 12mm philips flat head | 7 | 4(7)+1(30)+2(37) | McMaster-Carr | 92010A122 | 100 | $7.56
1 | M3 x 10mm philips flat head | 4 | 1(13)+3(27) | McMaster-Carr | 92010A120 | 100 | $7.10
1 | M6 x 1.0 x 6mm set screw point end | 1 | 1(23) | McMaster-Carr | 91217A210 | 25 | $3.63
4 | M5 x 25mm round coupling nut | 2 | 1(5)+1(6) | Belmetric.com | NROUND5X20CLZ | 1 | $0.93 | https://www.belmetric.com/metric-round-coupling-nut-c-3_280_1205/nround5x20clz-standoff-round-coupler-zinc-p-8321.html
1 | 6mm x 55mm Al tube | 2 | 2(6) | McMaster-Carr | 88605K25 | 2 | $5.01 | Brass
4 | M5 x 80mm screw full thread | 0 | 1(8) | McMaster-Carr | 91290A201 | 1 | $2.13 | Socket head Alloy Steel Only 70mm long
1 | coil compression spring 7.7mm x 35mm x 0.7mm | 1 | 1(7) | McMaster-Carr | 9657K348 | 12 | $10.77 | .3"X1.5"X.022"
1 | Extension spring 5.mm x 18.3mm x 0.45mm loop ends | 1 | 1(36) | McMaster-Carr | 9654K956 | 12 | $8.35 | .188"X.75x.018
1 | Steel Ball 5mm dia | 1 | 1(23) | McMaster-Carr | 1598K26 | 50 | $8.27
1 | M5 washer | 1 | 1(9) | McMaster-Carr | 93475A240 | 100 | $2.57
4 | M5 knurled nut | 1 | 1(9) | McMaster-Carr | 90368A250 | 1 | $3.01
1 | M4 x 20mm knurled screw | 1 | 1(38) | McMaster-Carr | 96016a129 | 10 | $6.00 | Plastic knob
 | M4-0.7mm | 6 |  | McMaster-Carr | 91828A231 | 100 | $2.45
 | M5-0.8mm | 2 |  | McMaster-Carr | 91828A241 | 100 | $5.55
 | Needle micrometer head 1-13mm travel 9.5mm mount(0.375") | 1 | 1(33) | ebay.com | China | 1 | $10.75 | https://www.ebay.com/itm/Round-Needle-Type-Thread-Micrometer-Head-Measurement-Measure-Tool-0-13mm-Range/161877562462?epid=1469976790
2 | M5 threaded rod | 80mm | 1(9) | McMaster-Carr | 90024A224 | 300mm | $5.48 | Part of camera lens focuser
Some points to note:
1. I couldn't find the M5x80mm screw used to focus the camera lens. I substituted a M5 threaded rod. This requires the M5 lock nut and using Locktite to keep the nut in place as a head.
2. For the aluminum tube used on this focuser I substituted brass.
3. In the "Qty (Where used)" column the parenthesis number references the page of Paul's pdf document where the part is installed.
4. Except where noted all materials are 18-8 stainless.
5. In Paul's pdf there isn't any specific page that shows inserting the M5 coupler into the focus slider. However it is shown on page 6.

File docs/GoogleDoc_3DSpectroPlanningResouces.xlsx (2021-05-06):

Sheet: Tom
Project | Part Name | Part Number | URL to part (wrapped) | Notes | Code
LowSpec Cal Lamp Injector | 28BYJ-48 Stepper Motor | 28BYJ-48 | https://www.amazon.com/gp/offer-listing/B01CP18J4A/ref=dp_olp_afts?ie=UTF8&condition=all | Can get as paired w/ UNL2003 Driver board
 | ULN2003 Stepper Driver | ULN2003 | Look below
 | Hall Effect Switch | KY-003 | https://www.amazon.com/gp/product/B06XHG9CYN/ref=ppx_yo_dt_b_asin_title_o07_s00?ie=UTF8&psc=1
 | Tiny Cylindrical Magnet
 | Arduino Nano/Uno/Mega |  | https://www.amazon.com/gp/product/B07WK4VG58/ref=ppx_yo_dt_b_asin_title_o00_s00?ie=UTF8&psc=1
 | Small Wood Screws | Various | Various
 | 2X5VDC Relay Board |  | https://www.amazon.com/SunFounder-Channel-Optocoupler-Expansion-Raspberry/dp/B00E0NTPP4
 | Cal Lamp | ? |  | Depends on what you want
 | Flat Lamp Grain of Wheat Bulb |  |  | 12 VDC Incandescent Bulbs
LowSpec Rotator | 28BYJ-48 Stepper Motor | 28BYJ-48 | https://www.amazon.com/gp/offer-listing/B01CP18J4A/ref=dp_olp_afts?ie=UTF8&condition=all | Can get as paired w/ UNL2003 Driver board
 | ULN2003 Stepper Driver | ULN2003 | Look below
 | Hall Effect Switch | KY-003 | https://www.amazon.com/gp/product/B06XHG9CYN/ref=ppx_yo_dt_b_asin_title_o07_s00?ie=UTF8&psc=1
 | Tiny Cylindrical Magnet
 | Arduino Nano/Uno/Mega |  | https://www.amazon.com/gp/product/B07WK4VG58/ref=ppx_yo_dt_b_asin_title_o00_s00?ie=UTF8&psc=1
 | GY-521 MPU 6050 6 DOF |  | https://www.amazon.com/MPU-6050-Accelerometer-Gyroscope-Converter-Compatible/dp/B081YNFZ5S
LowSpec Focuser | 28BYJ-48 Stepper Motor | 28BYJ-48 | https://www.amazon.com/gp/offer-listing/B01CP18J4A/ref=dp_olp_afts?ie=UTF8&condition=all | Can get as paired w/ UNL2003 Driver board
 | ULN2003 Stepper Driver | ULN2003 | Look below
 | Hall Effect Switch | KY-003 | https://www.amazon.com/gp/product/B06XHG9CYN/ref=ppx_yo_dt_b_asin_title_o07_s00?ie=UTF8&psc=1
 | Tiny Cylindrical Magnet
 | Arduino Nano/Uno/Mega |  | https://www.amazon.com/gp/product/B07WK4VG58/ref=ppx_yo_dt_b_asin_title_o00_s00?ie=UTF8&psc=1
Resistor packs | https://www.amazon.com/gp/product/B07L851T3V/ref=ppx_yo_dt_b_asin_title_o02_s00?ie=UTF8&psc=1
16 bit ADC | https://www.amazon.com/gp/product/B07VPFLSMX/ref=ppx_yo_dt_b_asin_title_o02_s00?ie=UTF8&psc=1
Wireless Transciever sockets | https://www.amazon.com/gp/product/B07KVSBQCS/ref=ppx_yo_dt_b_asin_title_o05_s00?ie=UTF8&psc=1
2pcs NRF24L01+PA+LNA RF Transceiver Module | https://www.amazon.com/gp/product/B07PBBC4H9/ref=ppx_yo_dt_b_asin_title_o05_s00?ie=UTF8&psc=1
5 PCS KY-040 Rotary Encoder Module Brick Sensor | https://www.amazon.com/gp/product/B015QSIRPK/ref=ppx_yo_dt_b_asin_title_o07_s01?ie=UTF8&psc=1
Easyget 5pcs Sets 28BYJ-48 ULN2003 5V Stepper Motor + ULN2003 Driver Board | https://www.amazon.com/gp/product/B072JDLF38/ref=ppx_yo_dt_b_asin_title_o00_s00?ie=UTF8&psc=1
Arduino Nano 33 BLE Sense with headers Mounted | https://www.amazon.com/gp/product/B07WXKDVTL/ref=ppx_yo_dt_b_asin_title_o01_s00?ie=UTF8&psc=1
McIgIcM Transistor Kit, BC337 BC327 2N2222 2N2907 2N3904 2N3906 S8050 S8550 A1015 C1815 Assortment, 10 Values, 200Pcs | https://www.amazon.com/gp/product/B06XCXX69F/ref=ppx_yo_dt_b_asin_title_o07_s00?ie=UTF8&psc=1
4PCS Breadboards Kit Include 2PCS 830 Point 2PCS 400 Point Solderless Breadboards for Arduino Proto Shield Distribution Connecting Blocks | https://www.amazon.com/gp/product/B07DL13RZH/ref=ppx_yo_dt_b_asin_title_o04_s00?ie=UTF8&psc=1
KeeYees 10pcs 4 Channels IIC I2C Logic Level Converter Bi-Directional Module 3.3V to 5V Shifter for Arduino (Pack of 10) | https://www.amazon.com/gp/product/B07LG646VS/ref=ppx_yo_dt_b_asin_title_o02_s00?ie=UTF8&psc=1
Organizer 10 Pack LM2596 DC to DC Buck Converter 3.0-40V to 1.5-35V Power Supply Step Down Module | https://www.amazon.com/gp/product/B07X751XD6/ref=ppx_yo_dt_b_asin_title_o02_s00?ie=UTF8&psc=1
UCTRONICS Numerical Control DC 6-55V to 0-50V 5A Step Down Stabilized Power Supply Constant Voltage Current Buck Power Converter Power Supply Adjustable Module | https://www.amazon.com/gp/product/B01LWXAC5E/ref=ppx_yo_dt_b_asin_title_o02_s00?ie=UTF8&psc=1
McIgIcM 5pcs Micro USB 5V 1A 18650 TP4056 Lithium Battery Charger Module Charging Board with Protection Dual Functions 1A Li-ion | https://www.amazon.com/gp/product/B06XQRQR3Q/ref=ppx_yo_dt_b_asin_title_o09_s00?ie=UTF8&psc=1
JBtek 4 Channel DC 5V Relay Module for Arduino Raspberry Pi DSP AVR PIC ARM | https://www.amazon.com/gp/product/B00KTEN3TM/ref=ppx_yo_dt_b_asin_title_o03_s00?ie=UTF8&psc=1
JBtek 8 Channel DC 5V Relay Module for Arduino Raspberry Pi DSP AVR PIC ARM | https://www.amazon.com/gp/product/B00KTELP3I/ref=ppx_yo_dt_b_asin_title_o03_s01?ie=UTF8&psc=1
Baomain Transistor MAC97A6 Bi-Directional Triac 600V 1A 15pack | https://www.amazon.com/gp/product/B00SUXPRZC/ref=ppx_yo_dt_b_asin_title_o03_s00?ie=UTF8&psc=1
5pack 9v Battery Clip with 2.1mm X 5.5mm Male DC Plug for Arduino by Corpco | https://www.amazon.com/gp/product/B01AXIEDX8/ref=ppx_yo_dt_b_asin_title_o01_s02?ie=UTF8&psc=1
Kalevel 120pcs Breadboards Jumper Wires Male to Female Jumper Wires Male to Male Jumper Wires Female to Female Jumper Wires Kit Long Ribbon Cable 20cm (m-m, f-f, m-f) | https://www.amazon.com/gp/product/B00M5WLZDW/ref=ppx_yo_dt_b_asin_title_o01_s02?ie=UTF8&psc=1
ARDUINO UNO R3 [A000066] | https://www.amazon.com/gp/product/B008GRTSV6/ref=ppx_yo_dt_b_asin_title_o02_s00?ie=UTF8&psc=1
Yosoo 5 pcs 12V 40W Reprap Ceramic Cartridge Heater For 3D Printer Prusa Mendel SHIPPING FROM US High quality | https://www.amazon.com/gp/product/B00O9S5BO4/ref=ppx_yo_dt_b_asin_title_o00_s00?ie=UTF8&psc=1
Sunshine Variable Resistor Assorted Kit 14 Value 280pcs Potentiometer | https://www.amazon.com/gp/product/B016UKOHFW/ref=ppx_yo_dt_b_asin_title_o05_s00?ie=UTF8&psc=1
Jameco Valuepro G/S(PT-6601)-R Single Pole Single Throw Off Momentary on 12V DC at 150 mA Tactile Pushbutton Switch | https://www.amazon.com/gp/product/B00D82M9LA/ref=ppx_yo_dt_b_asin_title_o07_s00?ie=UTF8&psc=1
KEYESTUDIO 20x4 LCD Display IIC/I2C/TWI 2004 Display for Arduino Controller r3 Mega 2560 Raspberry Pi Avr Stm32 | https://www.amazon.com/gp/product/B01799UUGS/ref=ppx_yo_dt_b_asin_title_o09_s00?ie=UTF8&psc=1
SCStyle 5 Meters GT2 2mm Pitch 6mm Wide Timing Belt for 3D Printer CNC | https://www.amazon.com/gp/product/B00F2IQNX8/ref=ppx_yo_dt_b_asin_title_o00_s00?ie=UTF8&psc=1
Aideepen DS3231SN RTC Module, 2PCS DS3231 AT24C32 IIC High Precision Real Time Clock Breakout Replace DS1307 for Arduino | https://www.amazon.com/Aideepen-DS3231SN-AT24C32-Precision-Breakout/dp/B07WJZ7NKM
Loads of ULN2003 and 28BYJ-48 and more | https://www.amazon.com/s?k=ULN2003&ref=nb_sb_noss_2
DaFuRui 5Pack GY-521 MPU-6050 Module 6 DOF 3 Axis Accelerometer Gyroscope Sensor Module 16 Bit AD Converter Data Output IIC I2C Compatible for Arduino | https://www.amazon.com/MPU-6050-Accelerometer-Gyroscope-Converter-Compatible/dp/B081YNFZ5S
SainSmart 8-Channel 5V Solid State Relay Module Board for Arduino Uno Duemilanove MEGA2560 MEGA1280 ARM DSP PIC | https://www.amazon.com/SainSmart-8-Channel-Duemilanove-MEGA2560-MEGA1280/dp/B006J4G45G?swrs=44BFEA7D78A5ECEF47DA221BF44ABD42
SunFounder Ultrasonic Module HC-SR04 Distance Sensor for Arduino R3 Mega2560 Duemilanove Nano Robot Rapsberry Pi 4B 3B+, 3B, 2 Model B & 1 Model B+ | https://www.amazon.com/SunFounder-Ultrasonic-Distance-Duemilanove-Rapsberry/dp/B00E0NXTJW

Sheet: Wayne
Pro Mini 5V | Not the SparkFun init.
ODroid
R-pi 3
R-pi 4
Mega 2560 r3 | Arduino Mega | 1
Arduino Uno |  | 2
Arduino Pro Mini 5V | Small Arduino + headers | 12
BOB-12009 | Bi-directinal level converter | 1
DEV-14352 | Qwic shield for Arduino | 2
BOB-14685 | Qwic Mux breakout 8 channels | 2
 | 100 mm I2C cables | 4
DEV-15794 | Qwic SHIM I2C for Rpi | 1
BOB-09118 | Opto-isolator breakout
 | Headers - various
18B20 | Maxim/Dallas one-wore temperature sensor | 5
SEN-12756 | Tripple Axis accelerometer breakout | 1
SEN-10167 | AOSONG DHT22 SENSOR HUMID/TEMP 5V DTL 2% MOD | 1
TMP117 | Qwic NIST temperature sensor | 1
Microbit | Card Micro Computer | 2
FM/FM Jumpers | pin to pin | numerous
M/M Jumpers | Breadboard jumpers | numerous

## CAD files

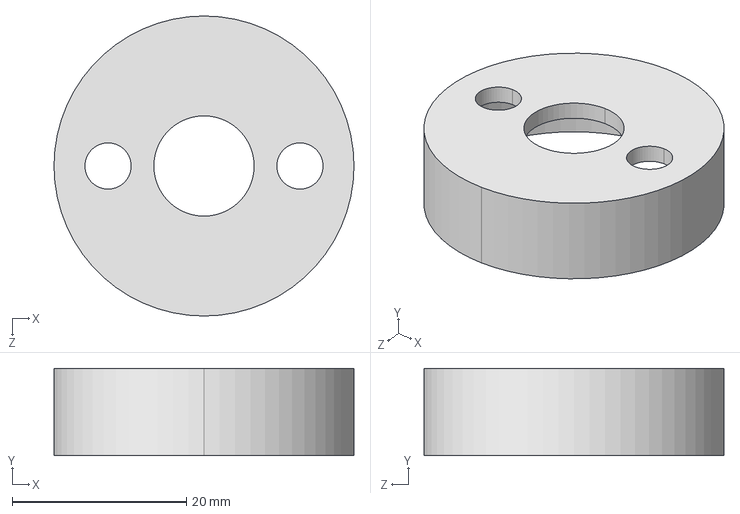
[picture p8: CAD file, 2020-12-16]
GregsRing/Gregs ring plug.STEP
34.4 x 10.0 x 34.4 mm

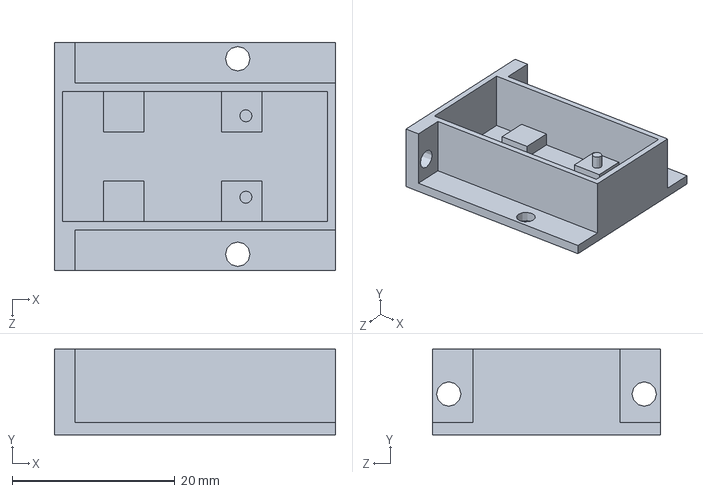
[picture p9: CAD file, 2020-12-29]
hall sensor housing/hall base.SLDPRT
34.5 x 10.5 x 28.0 mm

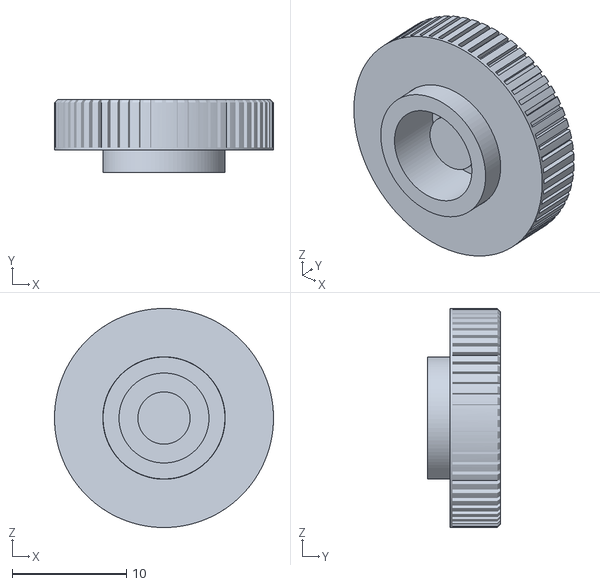
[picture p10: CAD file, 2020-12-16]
Knobs/Knob_10.STL
19.2 x 6.35 x 19.2

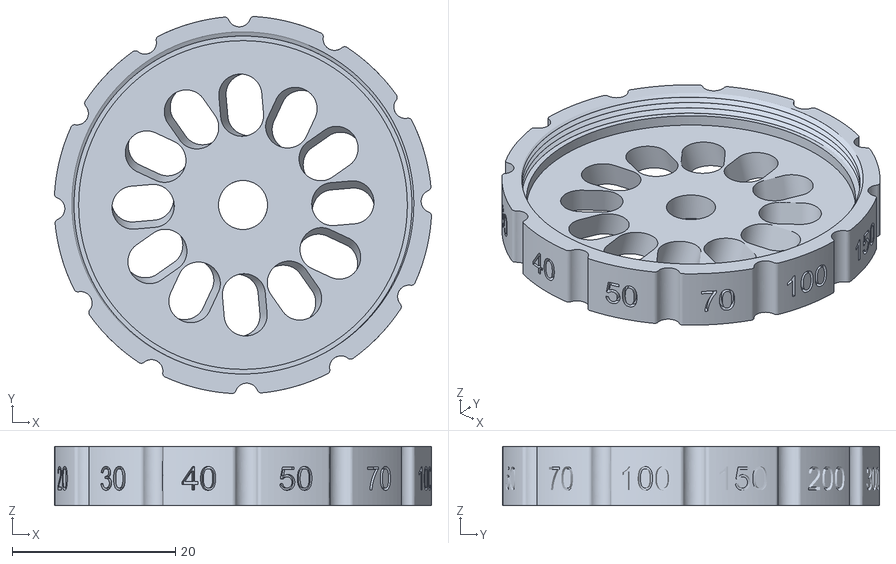
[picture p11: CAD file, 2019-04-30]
LowSpec 2.0 Components/17_2ovio_holder_slit_disc.stl
46.1 x 46.1 x 7.25

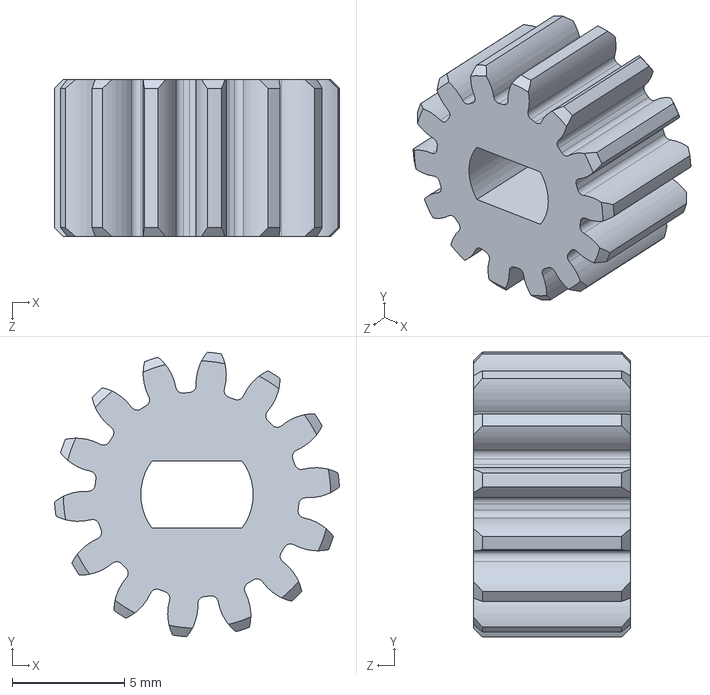
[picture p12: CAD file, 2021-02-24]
NA1/grating stage/32-14 motor gear.SLDPRT
12.7 x 12.7 x 7.00 mm

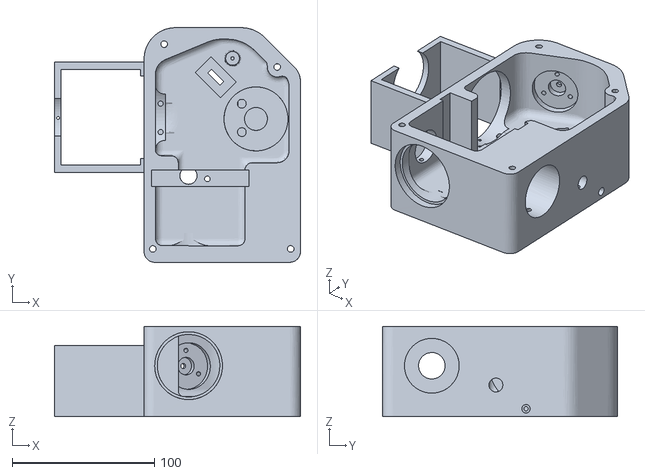
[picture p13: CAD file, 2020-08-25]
NA1/Lowspec3E2.stl
173.0 x 165.0 x 63.6

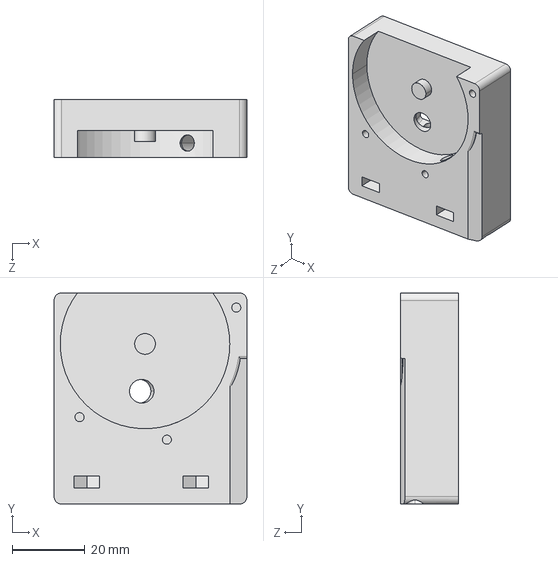
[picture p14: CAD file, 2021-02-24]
NA1/New OVIO holder/New OVIO holder.STEP
53.0 x 58.0 x 16.0 mm

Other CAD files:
SolidWorks version LowSpec_3/Optical components.step.SLDASM
SolidWorks version LowSpec_3/15_holder_guide_lens_AC127-030-A.step.SLDASM
SolidWorks version LowSpec_3/OVIO slit plate (1) (2).step.SLDASM
SolidWorks version LowSpec_3/LowSpec_3 v1.step.SLDASM
SolidWorks version LowSpec_3/16_jeulin_platform.step.SLDASM
SolidWorks version LowSpec_3/01_main_body.step.SLDPRT
SolidWorks version LowSpec_3/turn table hardware.step.SLDASM
SolidWorks version LowSpec_3/Grating holder.step.SLDASM
SolidWorks version LowSpec_3/10_main_mirror_holder.step.SLDPRT
SolidWorks version LowSpec_3/Jeulin slit module.step.SLDASM
SolidWorks version LowSpec_3/focusser.step.SLDASM
GregsRing/Gregs ring cap.SLDDRW
GregsRing/Gregs ring cap.SLDPRT
GregsRing/Gregs ring cap.STEP
GregsRing/Gregs ring cap.STL
GregsRing/Gregs ring plug.SLDDRW
GregsRing/Gregs ring plug.SLDPRT
GregsRing/Gregs ring plug.STL
Knobs/Knob.SLDPRT
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

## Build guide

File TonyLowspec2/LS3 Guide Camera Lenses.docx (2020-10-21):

All frames T4 camera; 30um Ovio slit; 17mm diameter lenses stopped to 13mm.

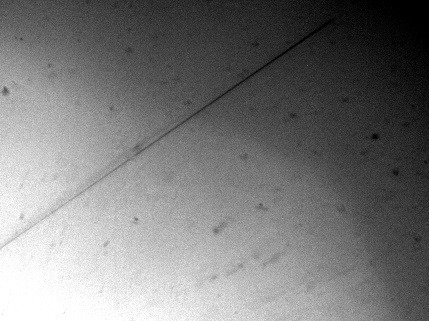
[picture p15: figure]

30 mm fl. OK for Lodestar

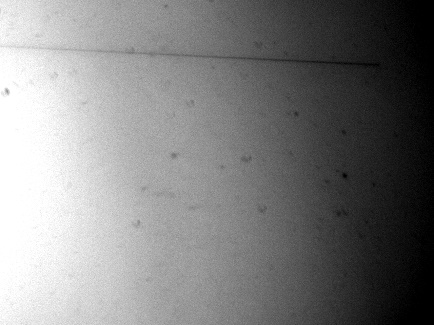
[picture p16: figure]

32 mm fl XXX

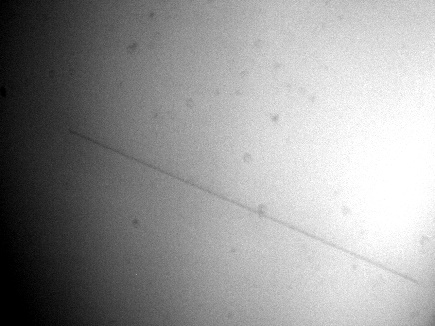
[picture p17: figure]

28 mm fl Slightly better, perhaps Lodestar for better field?

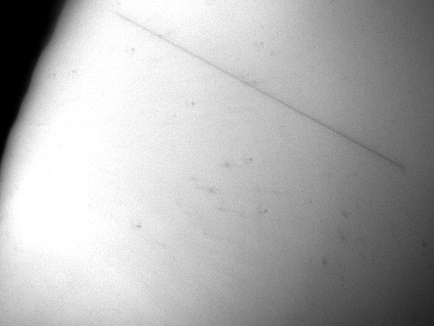
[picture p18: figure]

26 mm fl Probably the best compromise for the T7. Good FoV

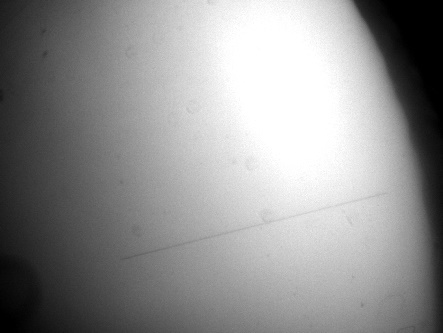
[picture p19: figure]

25 mm fl Wortyh trying for the T7.

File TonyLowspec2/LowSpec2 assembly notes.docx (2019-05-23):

My apologies, but I missed some hardware for the LowSpec2.

Specifically you'll need to get Qty 6 of an M4-0.7mm nuts. These are for the cover bolts and the thumb screw that holds the guide camera.

Also don't forget to get Qty 2 of an M5-0.8mm nuts for the Focus threaded rod.

Both can be purchased at Home Depot or Lowe's.

Also if your going to do much of this stuff I would go to Harbor Freight and buy a drill set that includes numbered, fractional and letter drill bits. These are not production drills but for plastics they will do.

To install the thumb screw nut drill out the existing hole with a "N" dull drill to a depth of about 1/8" Then tap the nut into place and glue. If you don't have an "N" drill use a 5/16" drill and glue. Also I filed the end of this thumb screw smooth so that it didn't scratch the nose of my guide camera.

Note on drilling plastic: on the cutting edge of the drill bit break the sharp edge so that it doesn't grab and drill all of the way through. See the attached image (enlarge if necessary). The idea is to scrape the plastic away rather than cut it away. Keep this drill just for plastics

.

I have been assembling the LowSpec2 with two different adhesives: To hold nuts in place I use Cyanoacrylate medium thick and use a spray Kicker. Hobby stores have this stuff. The Kicker accelerates the cure of the CA. The other adhesive is two part epoxy. Again check the hobby store. I used epoxy to secure the two rings on the telescope port and the camera port.

In order to make the grating assembly rotate easily, I had to file a few tight spots. Also if your going to make this assembly removable as in Tony's design you'll need to drill out the locations on the assembly base to accept the M3 screws. I used a 1/4" drill and went only deep enough to seat the nut flush. with the top surface. Again, dull the drill or you'll go right through (don't ask me how I know).

With Tony's hatch on the lid I used two of the M3 x 10mm flat head screws. Drilling out the lid to tap the M3 screw (#39) and drilling the hatch cover with a #31 drill. No need to dull drill as these are both drilled through. You can also use the 1/4" dulled drill to countersink the hatch holes a little for the flat heads. It isn't necessary to tap the M3 holes in the lid as the screws self tap easily.

Also when tapping the M4 holes I have found that the printed hole is a little small so I enlarged these using a #29 drill first.

I just received the metal T2 extension rings and I think that using a 5mm one as the active mating section on both the camera and telescope ports is a good idea. That will preserve the plastic threads.


Jerry

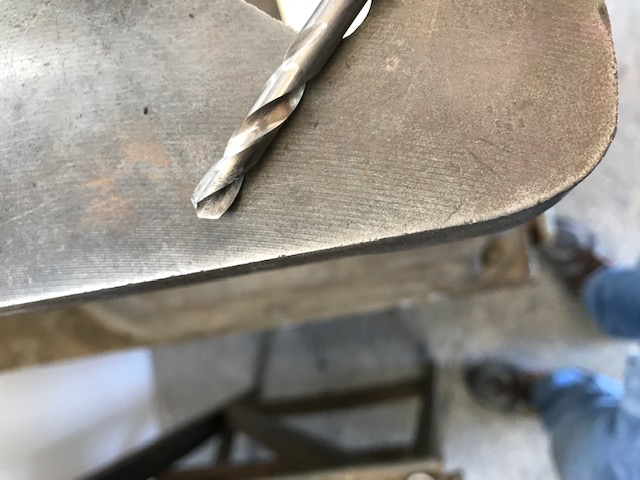
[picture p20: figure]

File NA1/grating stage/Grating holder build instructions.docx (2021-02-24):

Grating holder for “Extrusion“ version of NA1

Feb. 3, 2021 Jerry Foote

There are 5 printed parts to the Grating holder: Base, geared stage, motor gear, grating mount and an optional “dummy” bearing.

Additional parts:

4mm x 2mm N52 disk magnets (6 each) (ebay)

3/8 flat washer 0.438 ID x 1.0” OD x .075 Zinc Plated flat washer from my collection

28BYJ-48 stepper motor

0.625” OD x 0.25” ID ball bearing if used

4-40 x ¼ screw

Gap filling CA glue

The “dummy” ball bearing can be printed and used in place of an actual ball bearing for testing.

Some of the printed parts need particular orientations when printing:

Geared stage: orient with the 4 magnet holes on the bed use support touching the bed.

Grating mount: orient with the bottom (“D” shaped hole) up and use Tree support.

Be sure and test fit all parts before gluing.

After printing the geared stage make sure that the side with the 4 holes is very flat by lightly sanding on a flat surface. If you use the Dummy ball bearing put this in before sanding.

Make sure that the washer fits the opening in the base. Washer specs are pretty loose and some trimming of the hole might be needed. The washer face should be just slightly above the base part. Washers are stamped and the top surface has rounded edges. This surface should placed down into the base with flat side up. Also before gluing the washer in place check that the bottom is flat without burs. Test that the geared stage fits on the base flat without wobble, sand flat where necessary. The washer is glued into the base with a few drops of the CA glue.

Installing the magnets is tricky as they have a love/hate relationship. For the grating holder magnet make sure it fits and then put a drop of glue in the hole and press home. Take another magnet and let it find its mate in the grating holder you just glued. Take a felt tip pen and mark the side that is up. Now add a drop of glue to the geared stage magnet hole and put the marked side of the magnet into the hole.

Place the four magnets on the washer. Push them together side by side and make sure that one doesn’t repel from another. After they are all next to each other mark the top surface of each magnet. One at a time glue each magnet into the geared stage with the marked side up and push it home. Do the same for the other three magnets.

The motor is mounted from the bottom of the base. I used only one screw (4-40 x ¼) to hold it in place during tests. Place the motor gear on the motor once installed.

In the final application the motor gear will need to be changed to accommodate the thickness of the mounting plate…TBD.

Performanc:

One step of the motor results in 0.2 degrees of grating rotation. Any position is repeatable (+/- .01 degree) provided that the direction of approach is always the same.

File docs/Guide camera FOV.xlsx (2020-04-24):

Guide camera field of view |  |  | =input
Telescope Aperture Diameter (mm) | Telescope Focal Ratio | Telescope Focal Length (mm) | Plate Scale (Arc-sec/mm) | Plate Scale (degrees/mm)
355.00 | 8.00 | 2840.00 | 72.63 | 0.0202
Guide Lens focal length (mm) | Distance to slit (mm) | Distance to Guide Camera (mm) | Guide Camera CCD width (mm) | FOV of Guide camera (minutes) | FOV of guide camera (arc-seconds)
30.00 | 60.00 | 60.00 | 10.00 | -12.10 | -726.29
Slit Width (micron) | Guide Camera Pixel dimension (micron) | Slit width as seen by guide camera (pixels) | Slit height as seen by guide camera (mm)
23.00 | 8.60 | 2.67 | 10.00

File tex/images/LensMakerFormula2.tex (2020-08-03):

\documentclass[10pt]{article}
\usepackage{pgf,tikz,pgfplots}
\pgfplotsset{compat=1.15}
\usepackage{mathrsfs}
\usetikzlibrary{arrows}
\pagestyle{empty}
\newcommand{\degre}{\ensuremath{^\circ}}
\begin{document}
\definecolor{qqwuqq}{rgb}{0,0.39215686274509803,0}
\definecolor{qqqqff}{rgb}{0,0,1}
\definecolor{uuuuuu}{rgb}{0.26666666666666666,0.26666666666666666,0.26666666666666666}
\definecolor{ududff}{rgb}{0.30196078431372547,0.30196078431372547,1}
\definecolor{ffqqqq}{rgb}{1,0,0}
\definecolor{xdxdff}{rgb}{0.49019607843137253,0.49019607843137253,1}
\begin{tikzpicture}[line cap=round,line join=round,>=triangle 45,x=1cm,y=1cm,scale=.2]
\begin{axis}[
x=1cm,y=1cm,
axis lines=middle,
ymajorgrids=true,
xmajorgrids=true,
xmin=-35.908428957138916,
xmax=55.117646309668594,
ymin=-21.91544157915341,
ymax=29.136905260878166,
xtick={-35,-30,...,55},
ytick={-20,-15,...,25},]
\clip(-35.908428957138916,-21.91544157915341) rectangle (55.117646309668594,29.136905260878166);
\draw [shift={(20,0)},line width=2pt,color=qqwuqq,fill=qqwuqq,fill opacity=0.10000000149011612] (0,0) -- (165.96375653207352:1.9436172654834343) arc (165.96375653207352:194.03624346792648:1.9436172654834343) -- cycle;
\draw [shift={(20,0)},line width=2pt]  plot[domain=2.896613990462929:3.3865713167166573,variable=\t]({1*20.615528128088304*cos(\t r)+0*20.615528128088304*sin(\t r)},{0*20.615528128088304*cos(\t r)+1*20.615528128088304*sin(\t r)});
\draw [shift={(-20,0)},line width=2pt]  plot[domain=-0.24497866312686423:0.24497866312686414,variable=\t]({1*20.615528128088304*cos(\t r)+0*20.615528128088304*sin(\t r)},{0*20.615528128088304*cos(\t r)+1*20.615528128088304*sin(\t r)});
\draw [line width=2pt] (-40,5)-- (0,5);
\draw [line width=2pt] (-19.514095683629144,5) -- (-20,4.416914820354969);
\draw [line width=2pt] (-19.514095683629144,5) -- (-20,5.583085179645031);
\draw [line width=2pt] (-40,-5)-- (0,-5);
\draw [line width=2pt] (-19.514095683629144,-5) -- (-20,-5.583085179645027);
\draw [line width=2pt] (-19.514095683629144,-5) -- (-20,-4.4169148203549655);
\draw [line width=2pt] (0,5)-- (20,0);
\draw [line width=2pt] (10.471396428315431,2.3821508929211404) -- (9.858581071505368,1.934324286021478);
\draw [line width=2pt] (10.471396428315431,2.3821508929211404) -- (10.141418928494627,3.0656757139785182);
\draw [line width=2pt] (0,-5)-- (20,0);
\draw [line width=2pt] (10.471396428315431,-2.3821508929211404) -- (10.141418928494627,-3.0656757139785182);
\draw [line width=2pt] (10.471396428315431,-2.3821508929211404) -- (9.858581071505368,-1.934324286021478);
\draw [line width=2pt,color=ffqqqq] (-40,0)-- (0,5);
\draw [line width=2pt,color=ffqqqq] (-19.51784789666552,2.560269012916807) -- (-19.92767718449983,1.9214174759986171);
\draw [line width=2pt,color=ffqqqq] (-19.51784789666552,2.560269012916807) -- (-20.072322815500176,3.0785825240013756);
\draw [line width=2pt,color=ffqqqq] (0,5)-- (30.13641626049038,3.1885778314936446);
\draw [line width=2pt,color=ffqqqq] (-40,0)-- (0,-5);
\draw [line width=2pt,color=ffqqqq] (-19.51784789666552,-2.560269012916807) -- (-20.072322815500176,-3.0785825240013756);
\draw [line width=2pt,color=ffqqqq] (-19.51784789666552,-2.560269012916807) -- (-19.92767718449983,-1.9214174759986171);
\draw [line width=2pt,color=ffqqqq] (0,-5)-- (30.05875237342711,-3.956499778327017);
\draw [->,line width=2pt] (-40,-5) -- (-39.994073757640564,-2.4032220370616653);
\draw [line width=2pt,color=qqqqff] (-40,-5)-- (0,0);
\draw [line width=2pt,color=qqqqff] (0,0)-- (30,0);
\draw [line width=2pt,color=qqqqff] (35.8835439031722,1.0139889937221238)-- (0,-5);
\draw [line width=2pt,color=qqqqff] (0,-5)-- (-2.477069759962774,-4.690366280004653);
\draw [line width=2pt,color=qqqqff] (-39.994073757640564,-2.4032220370616653)-- (0,-5);
\begin{scriptsize}
\draw [fill=xdxdff] (130.40312238249933,0) circle (2.5pt);
\draw[color=xdxdff] (-35.64927998840779,29.88195854598015) node {$A$};
\draw [fill=ffqqqq] (20,0) circle (2.5pt);
\draw[color=ffqqqq] (20.71562071061181,1.5699337121047707) node {$f_{1}$};
\draw [fill=xdxdff] (0,5) circle (2.5pt);
\draw[color=xdxdff] (0.5020011495840906,6.364189633630578) node {$C$};
\draw [fill=xdxdff] (0,-5) circle (2.5pt);
\draw[color=xdxdff] (0.5020011495840906,-3.6130456625177243) node {$D$};
\draw [fill=ududff] (-40,5) circle (2.5pt);
\draw[color=ududff] (-35.64927998840779,29.88195854598015) node {$F$};
\draw [fill=ududff] (-40,-5) circle (2.5pt);
\draw [fill=xdxdff] (-40,0) circle (2.5pt);
\draw[color=xdxdff] (-35.64927998840779,29.88195854598015) node {$H$};
\draw [fill=ududff] (30.13641626049038,3.1885778314936446) circle (2.5pt);
\draw[color=ududff] (30.628068764577325,4.550146852512706) node {$I$};
\draw [fill=ududff] (30.05875237342711,-3.956499778327017) circle (2.5pt);
\draw[color=ududff] (30.563281522394544,-2.576449787593225) node {$J$};
\draw [fill=ududff] (-39.994073757640564,-2.4032220370616653) circle (2.5pt);
\draw[color=ududff] (-34.09438617602105,29.88195854598015) node {$OffAxis$};
\draw [fill=uuuuuu] (0,0) circle (2pt);
\draw[color=uuuuuu] (0.5020011495840906,1.2459975011908648) node {$K$};
\draw [fill=xdxdff] (30,0) circle (2.5pt);
\draw[color=xdxdff] (30.498494280211762,1.375571985556427) node {$L$};
\draw [fill=ududff] (35.8835439031722,1.0139889937221238) circle (2.5pt);
\draw[color=ududff] (36.394133318844844,2.4121678604809262) node {$M$};
\draw [fill=xdxdff] (-2.477069759962774,-4.690366280004653) circle (2.5pt);
\draw[color=xdxdff] (-1.959914053361593,-3.2891094516038186) node {$N$};
\draw[color=qqwuqq] (22.52966349172968,0.46855059499749047) node {$\alpha = 28.07\textrm{\degre}$};
\end{scriptsize}
\end{axis}
\end{tikzpicture}
\end{document}

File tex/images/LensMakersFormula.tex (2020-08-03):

\documentclass[10pt]{article}
\usepackage{pgf,tikz,pgfplots}
\pgfplotsset{compat=1.15}
\usepackage{mathrsfs}
\usetikzlibrary{arrows}
\pagestyle{empty}
\begin{document}
\definecolor{ffqqqq}{rgb}{1,0,0}
\definecolor{ududff}{rgb}{0.30196078431372547,0.30196078431372547,1}
\definecolor{xdxdff}{rgb}{0.49019607843137253,0.49019607843137253,1}
\begin{tikzpicture}[line cap=round,line join=round,>=triangle 45,x=1cm,y=1cm,scale=0.1]
\begin{axis}[
x=1cm,y=1cm,
axis lines=middle,
ymajorgrids=true,
xmajorgrids=true,
xmin=-46.90615970627141,
xmax=31.146046792312863,
ymin=-26.24603536548495,
ymax=34.95310764037028,
xtick={-45,-40,...,30},
ytick={-25,-20,...,30},]
\clip(-46.90615970627141,-26.24603536548495) rectangle (31.146046792312863,34.95310764037028);
\draw [shift={(20,0)},line width=2pt]  plot[domain=2.896613990462929:3.3865713167166573,variable=\t]({1*20.615528128088304*cos(\t r)+0*20.615528128088304*sin(\t r)},{0*20.615528128088304*cos(\t r)+1*20.615528128088304*sin(\t r)});
\draw [shift={(-20,0)},line width=2pt]  plot[domain=-0.24497866312686423:0.24497866312686414,variable=\t]({1*20.615528128088304*cos(\t r)+0*20.615528128088304*sin(\t r)},{0*20.615528128088304*cos(\t r)+1*20.615528128088304*sin(\t r)});
\draw [line width=2pt] (-40,5)-- (0,5);
\draw [line width=2pt] (-19.41752084702549,5) -- (-20,4.301025016430589);
\draw [line width=2pt] (-19.41752084702549,5) -- (-20,5.698974983569415);
\draw [line width=2pt] (-40,-5)-- (0,-5);
\draw [line width=2pt] (-19.41752084702549,-5) -- (-20,-5.698974983569415);
\draw [line width=2pt] (-19.41752084702549,-5) -- (-20,-4.301025016430589);
\draw [line width=2pt] (0,5)-- (20,0);
\draw [line width=2pt] (10.56508778174922,2.358728054562697) -- (9.830473665475225,1.821894661900931);
\draw [line width=2pt] (10.56508778174922,2.358728054562697) -- (10.169526334524761,3.1781053380990754);
\draw [line width=2pt] (0,-5)-- (20,0);
\draw [line width=2pt] (10.56508778174922,-2.358728054562697) -- (10.169526334524761,-3.1781053380990754);
\draw [line width=2pt] (10.56508778174922,-2.358728054562697) -- (9.830473665475225,-1.821894661900931);
\draw [line width=2pt,color=ffqqqq] (-40,0)-- (0,5);
\draw [line width=2pt,color=ffqqqq] (-19.422018822856476,2.572247647142942) -- (-19.91330282342847,1.8064225874277728);
\draw [line width=2pt,color=ffqqqq] (-19.422018822856476,2.572247647142942) -- (-20.086697176571526,3.193577412572229);
\draw [line width=2pt,color=ffqqqq] (0,5)-- (30.13641626049038,3.1885778314936446);
\draw [line width=2pt,color=ffqqqq] (-40,0)-- (0,-5);
\draw [line width=2pt,color=ffqqqq] (-19.422018822856476,-2.572247647142942) -- (-20.086697176571526,-3.193577412572229);
\draw [line width=2pt,color=ffqqqq] (-19.422018822856476,-2.572247647142942) -- (-19.91330282342847,-1.8064225874277728);
\draw [line width=2pt,color=ffqqqq] (0,-5)-- (30.05875237342711,-3.956499778327017);
\begin{scriptsize}
\draw [fill=xdxdff] (130.40312238249933,0) circle (2.5pt);
\draw[color=xdxdff] (-46.595504158018336,35.84624234159786) node {$A$};
\draw [fill=xdxdff] (20,0) circle (2.5pt);
\draw[color=xdxdff] (20.583758151708423,1.6741320337599173) node {$B$};
\draw [fill=xdxdff] (0,5) circle (2.5pt);
\draw[color=xdxdff] (0.624139176448564,6.6446208058090726) node {$C$};
\draw [fill=xdxdff] (0,-5) circle (2.5pt);
\draw[color=xdxdff] (0.624139176448564,-3.296356738289239) node {$D$};
\draw [fill=ududff] (-40,5) circle (2.5pt);
\draw[color=ududff] (-39.372762661134416,6.6446208058090726) node {$F$};
\draw [fill=ududff] (-40,-5) circle (2.5pt);
\draw[color=ududff] (-39.372762661134416,-3.296356738289239) node {$G$};
\draw [fill=xdxdff] (-20,0) circle (2.5pt);
\draw[color=xdxdff] (-19.413143685874566,1.6741320337599173) node {$E$};
\draw [fill=xdxdff] (-40,0) circle (2.5pt);
\draw[color=xdxdff] (-39.372762661134416,1.6741320337599173) node {$H$};
\draw [fill=ududff] (30.13641626049038,3.1885778314936446) circle (2.5pt);
\draw[color=ududff] (30.757727356996522,4.8583514033539075) node {$I$};
\draw [fill=ududff] (30.05875237342711,-3.956499778327017) circle (2.5pt);
\draw[color=ududff] (30.602399582869985,-2.2867262064667537) node {$J$};
\end{scriptsize}
\end{axis}
\end{tikzpicture}
\end{document}

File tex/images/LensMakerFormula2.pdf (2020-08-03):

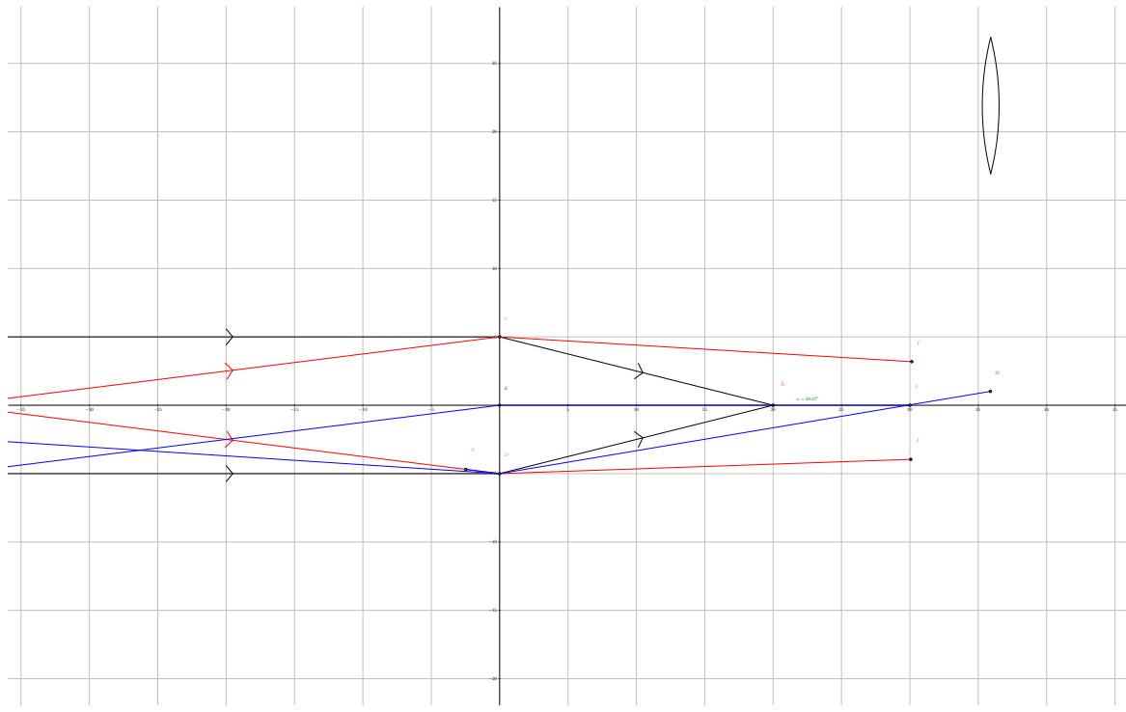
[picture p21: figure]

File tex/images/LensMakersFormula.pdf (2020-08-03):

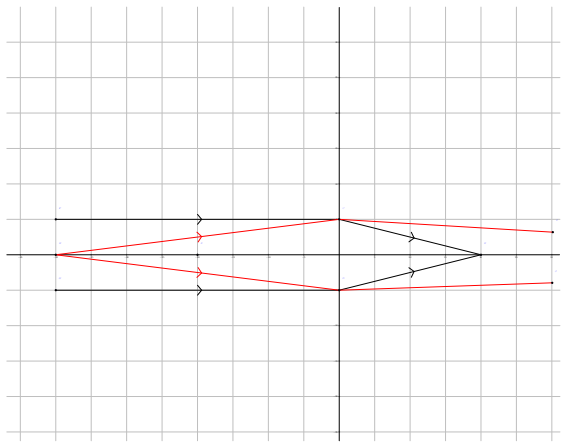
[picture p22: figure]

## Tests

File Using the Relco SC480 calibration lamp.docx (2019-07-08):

Using the Relco SC480 calibration lamp

Jerry Foote 07/08/2019

The Relco calibration lamp is a useful source of calibration lines having both Neon and Argon gas. This lamp is used in Shelyak’s Alpy and Lisa spectrographs calibration units.

We have been powering these lamps from a small high voltage power supply out of China.

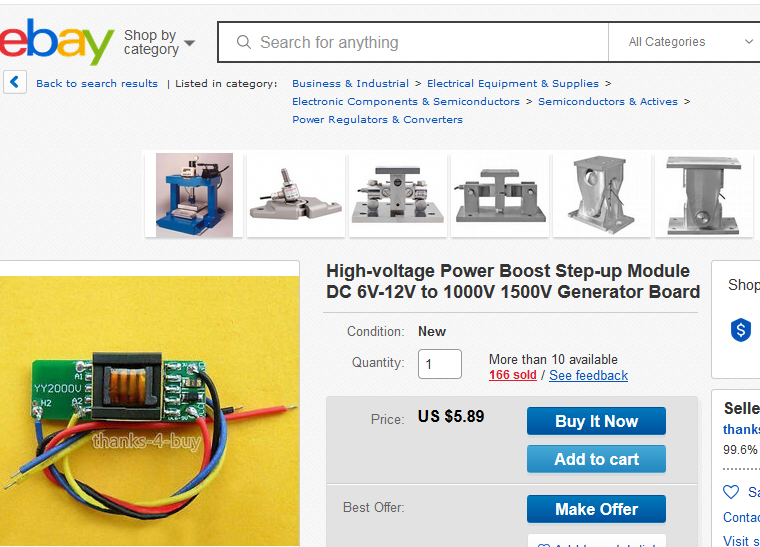
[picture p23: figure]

Tony Rodda and I have been working with the Relco lamps and this supply and have found that specific connections must be used in order to keep the lamp lit. Specifically use the terminals A1 and A2 to connect to the lamp( not A1 & H2). There isn’t a need for a series resistor in the high voltage circuit to limit current.

Even though the spec’s indicate that it can be powered from 12V, the lamp will start to dim appreciably after only a short time. I think that the drive MOSFET is over heating. If however you power it from 9V it will give good luminance and continue to operate. Tony has operated the system for over 4 hours on a single common 9V battery.

The emission spectra is here:

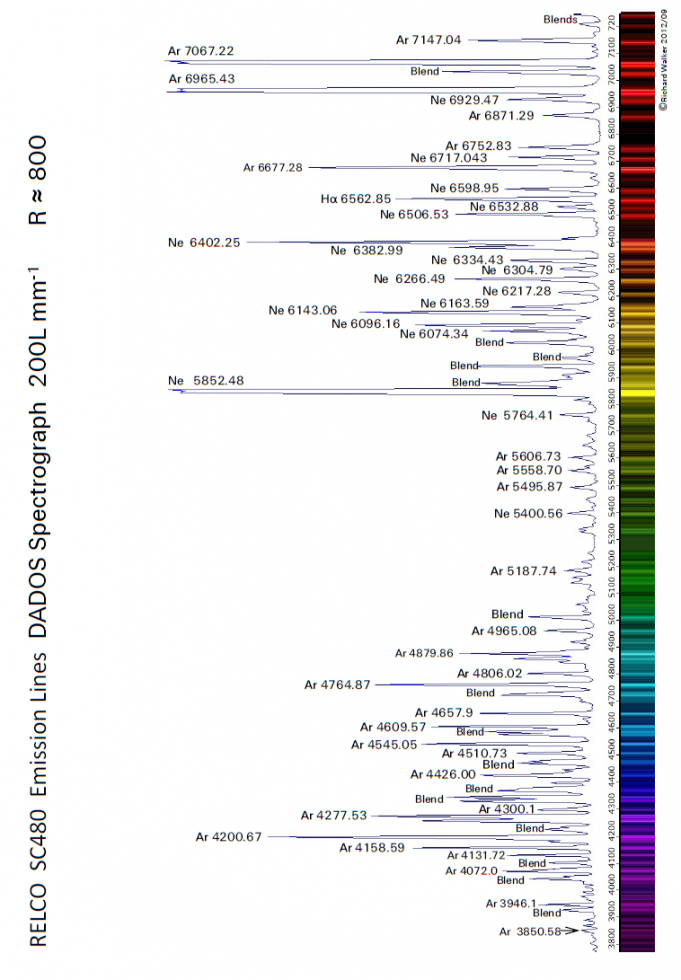
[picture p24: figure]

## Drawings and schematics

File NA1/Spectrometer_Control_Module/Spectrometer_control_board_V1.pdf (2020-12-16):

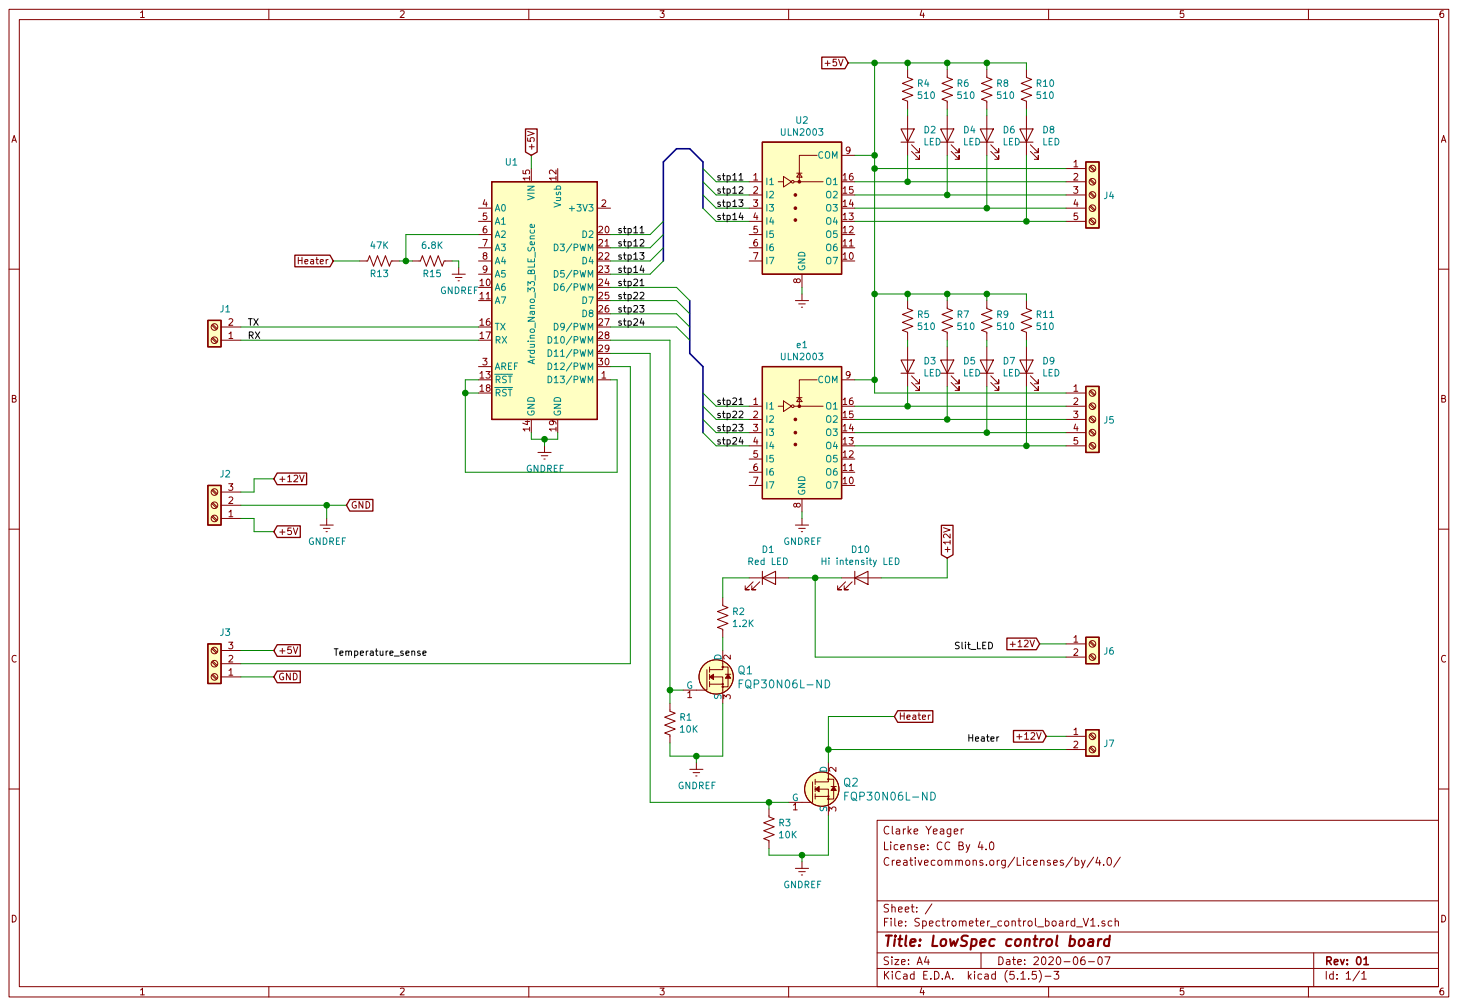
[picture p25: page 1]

Clarke Yeager
License: CC By 4.0
File: Spectrometer_control_board_V1.sch Sheet: / Creativecommons.org/Licenses/by/4.0/

Id: 1/1 Title: LowSpec control board

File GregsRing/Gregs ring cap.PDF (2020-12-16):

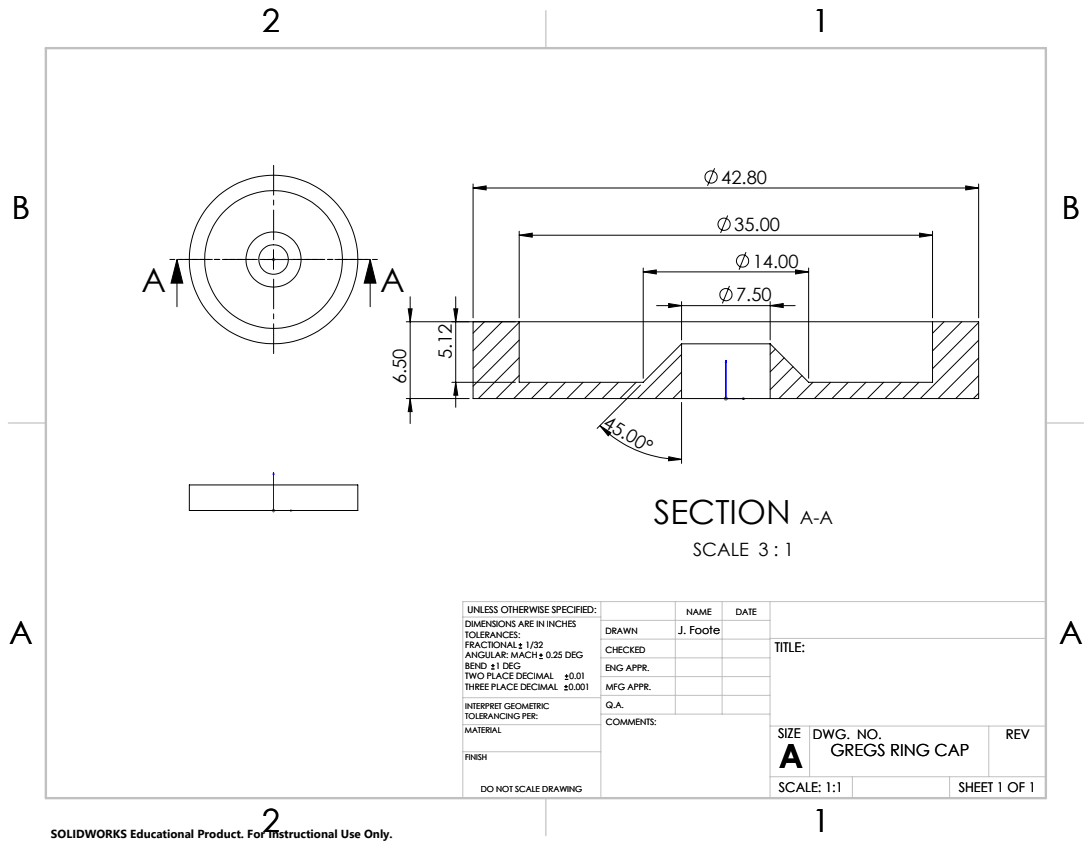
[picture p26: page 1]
SECTION A-A; SCALE 3 : 1; DO NOT SCALE DRAWING; SCALE: 1:1; SHEET 1 OF 1

UNLESS OTHERWISE SPECIFIED: | | NAME | DATE
DIMENSIONS ARE IN INCHES DIMENSIONS ARE IN INCHES TOLERANCES: TOLERANCES: FRACTIONAL 1/32 FRACTIONAL 1/32 ANGULAR: MACH 0.25 DEG ANGULAR: MACH 0.25 DEG BEND 1 DEG BEND 1 DEG TWO PLACE DECIMAL TWO PLACE DECIMAL 0.01 0.01 THREE PLACE DECIMAL 0.001 THREE PLACE DECIMAL 0.001 | DRAWN | J. Foote

CHECKED | | | TITLE:

ENG APPR.
MFG APPR.

INTERPRET GEOMETRIC INTERPRET GEOMETRIC TOLERANCING PER: TOLERANCING PER: | Q.A.

SIZE
DWG. NO.
GREGS RING CAP

SOLIDWORKS Educational Product. For Instructional Use Only.

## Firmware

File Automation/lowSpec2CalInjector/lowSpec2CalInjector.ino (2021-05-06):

///**************************************************
// *            lowSpec2CalInjector.ino             *
// **************************************************
// *      Written by: Thomas C. Smtih               *
// *      Created on: 20200323                      *
// **************************************************
// *    Revision history:                           *
// *    - Initial relase, version 1.0               *
// *    - 20200324 decided to create using standard *
// *      stepper driver instead of AccelStepper    *
// *    - 20200731 modified the slit lamp off       *
// *      from '9' to '7' so numerics are in order. *
// *      Added more info to the status command.    *
// *      Created a listing of functions.           *
// *    - 20200806 repaired the serial comms        *
// *    - 20200807 added PWM to slit lamp control   *
// **************************************************/

///**************************************************
// *    Functions:   (In coded order)               *
// **************************************************
// *    homeMotor()                                 *
// *    toggleAutoHome()                            *
// *    driveIN()                                   *
// *    driveOUT()                                  *
// *    runTo()                                     *
// *    resetCurrentStep()                          *
// *    doCommandEvaluation()                       *
// *    getStep()                                   *
// *    getStatus() not used yet                    *
// *    doAction()                                  *
// *    serialEvent()                               *
// *    showHelp()                                  *
// *    setup()                                     *
// *    loop()                                      *
// **************************************************/

///**************************************************
// *            Serial Command Protocol             *
// **************************************************
// *  A = toggle AutoHome feature                   *
// *  H = home the injector                         *
// *  L = toggle LOCAL commands for serial ECHO     *
// *  I = drive inward, CW from above motor shatf   *
// *  O = drive outward, CCW from above motor shaft *
// *  M = move  to the position value sent          *
// *  C = cal lamp relay ON                         *
// *  5 = cal lamp relay OFF                        *
// *  F = flat lamp relay ON                        *
// *  6 = flat lamp relay OFF                       *
// *  S = slit lamp LED ON with PWM                 *
// *  7 = slit lamp LED OFF                         *
// *  R = change speed of motor                     *
// *  T = test all three lamps                      *
// *  Z = reset the zero point w/ homing            *
// *  0 = (zero) get step                           *
// *  ? = brief help on commands                    *
// *************************************************/

///**************************************************
// *                Arduino Pinout                  *
// **************************************************
// *  1)  Injector Stepper Motor                    *
// *      Arduino   ->  ULN2003 Driver              *
// *      -------       --------------              *
// *     Ext.+5VDC  ->  (+) 5-12 pin                *
// *        GND     ->  (-) 5-12 pin                *
// *        D8      ->  ULN2003 IN1                 *
// *        D9      ->  ULN2003 IN2                 *
// *        D10     ->  ULN2003 IN3                 *
// *        D11     ->  ULN2003 IN4                 *
// *  - - - - - - - - - - - - - - - - - - - - - - - *
// *  2)  Lamp Relay Module                         *
// *      Arduino   ->  Relay Board                 *
// *      -------       ---------------             *
// *        +5 VDC  ->  Relay VCC                   *
// *        GND     ->  Relay GND                   *
// *        D5      ->  Slit LED                    *
// *        D3      ->  Cal Relay IN1               *
// *        D4      ->  Flat Relay IN2              *
// *  - - - - - - - - - - - - - - - - - - - - - - - *
// *  3)  Optional Pinout                           *
// *      Arduino   ->  Device Pin                  *
// *      -------       -----------------           *
// *        D2          Hall Switch indicator LED   *
// **************************************************/

///**************************************************
// *                  Program Flow                  *
// **************************************************
// *  - Start by creating the stepper object        *
// *  - Initialize variables and run setup()        *
// *  - Read the current Hall switch status         *
// *  - If switch not triggered then HOME the motor *
// *  - Wait for incomming serial command character *
// *  - Move either IN to 0 or OUT to maxSteps      *
// *  - Mxxxx moves to the specified step ('-xxxx'  *
// *    means drive to the inward step relative to  *
// *    the 0 or homed position)                    *
// *  - If command is '0'(zero) then show status    *
// *  - If command is '?' then display command list *
// *  - Slit LED will be PWM controllable on Pins 3,* <- this is due to those pins sharing 
// *      5, 6, 9, 10, and 11. 5&6 not advisable    *    timers with millis() and delay()
// **************************************************/ 

///**************************************************
// *            User Defined Variables              *
// **************************************************/
const int switchLEDPin        = 2;                          // remote hall switch indicator LED (optional)
const int FlatRelayPin        = 3;                          // Flat lamp relay pin
const int CalRelayPin         = 4;                          // Cal lamp relay pin
const int SlitLEDPin          = 5;                          // LED to illuminate the slit
const int hallSwitchPin       = 7;                          // hall sensor pin
const int motorPinIN1         = 8;                          // IN-1 pins on UL2003 board
const int motorPinIN2         = 9;                          // IN-2 pins on UL2003 board
const int motorPinIN3         = 10;                         // IN-3 pins on UL2003 board
const int motorPinIN4         = 11;                         // IN-3 pins on UL2003 board
const int maxSteps            = -15000; //16384;            // abs maximum steps from homed (0) to fully inserted

int speedToRun                = 1000;                       // speed to run <= 2000 steps/sec
const int testDelay           = 3000;                       // delay in seconds while doing a lamp test
bool boolLocalCommands        = true;                       // flag to display local verbose replies
bool autoHome                 = false;                      // flag for autohome on start
///**************************************************
// *        END of User Defined Variables           *
// **************************************************/

// **************************************************
// *            Include Stepper Object              *
// **************************************************/
#include <Stepper.h>

///**************************************************
// *      Initialize Non-User Defined Variables     *
// *              DO NOT NODIFY THESE               *
// **************************************************/
int stepCount = 0;                                          // number of steps the motor has taken
//const float STEPS_PER_REV     = 32;                         // motor steps ignoring the gearing
//const float GEAR_RED          = 64;                         // approximate reduction of 64:1
//const float STEPS_PER_REV_OUT = STEPS_PER_REV * GEAR_RED;   // includes reduction
const float STEPS_PER_REV_OUT = 32 * 64;   // includes reduction

int hallSwitchState           = 0;                          // holds the current switch state
int currentStep               = 0;                          // step counter, same as stepper.currentPosition()
int deltaSteps                = 0;                          // steps to move if not all IN or all OUT
bool bolHomeFound             = 0;                          // used to prevent continuious homming
String inputString            = "";                         // command string created from serial input
bool stringComplete           = false;                      // whether the string is complete                                     
String arrCommand[2];                                       // array holding command segments
//const String helpCommands = " A->toggle AutoHome, , L->toggel Local commands w/ECHO,\n I->full inward O->full outward, Mxxxx->Move To xxxx,\n Rxxxx->Change speed to xxxx,\n F->Flat lamp ON, 5->Flat lamp OFF, C->Cal lamp ON,\n 6->Cal lamp OFF, S->Slit LED ON, 7->Slit LED OFF,\n 0->Step Status, T->Test all lamps, ?->this help";
const String helpCommands = " A=Toggle AutoHome, L=Toggel Local w/ECHO,\n I=Inward O=Outward, Mxxxx=Move To xxxx,\n Rxxxx=Speed to xxxx,\n F=Flat ON, 5=Flat OFF, C=Cal ON,\n 6=Cal OFF, Sxxx=Slit PWM, 7=Slit OFF,\n 0=Step, T=Test lamps, ?=Help";

int SlitPWM                   = 0;                        // initally set to full off but adjustable
// step pins are energized in this patterns for forward stepping 1-3-2-4
//Stepper stepper(STEPS_PER_REV,8,10,9,11);                   // order is to be blue-yellow-pink-orange
Stepper stepper(32,8,10,9,11);                   // order is to be blue-yellow-pink-orange

int checkSwitchState(){
  // check the current state of the hall switch and return it as 0-not triggered or 1-triggered
  hallSwitchState = digitalRead(hallSwitchPin);
  if (hallSwitchState = 0){           // not triggered
    bolHomeFound = false;
    digitalWrite(switchLEDPin, LOW);  // turn off remote hall switch LED if installed
    return 0;
  }
  else {                              // triggered
    bolHomeFound = true;
    digitalWrite(switchLEDPin, HIGH); // turn on remote hall switch LED if installed
    return 1;
  }
}

void homeMotor(){
  // first check current hall switch state and if it is not ON (HOMED)
  // then drive motor outwards until hall switch triggers (HOMED)
  stepper.setSpeed(speedToRun);
  hallSwitchState = digitalRead(hallSwitchPin);
  if (hallSwitchState == 0){
    // motor is HOME so don't do anything but zero the step counter
    currentStep = 0;
    bolHomeFound = true;
    digitalWrite(switchLEDPin, HIGH);
    Serial.println("Motor is already homed!");
    return;
  }
  else {
     // motor is not at home so drive it there slowly with a recheck
     // by driving inward for XX steps and then back outward until
     // hall switch triggers
     while (digitalRead(hallSwitchPin) != 0){
       // drive outward and recheck
       stepper.step(50);
       checkSwitchState();
     }
      // now reset the counter
      stepCount = 0;  // zero the counter once homed 
      currentStep = 0;
      if (boolLocalCommands == true){
        Serial.println("Motor stepCount is now " + String(stepCount));
      }
      bolHomeFound = true;  
      digitalWrite(switchLEDPin, HIGH);  
   }
}

void toggleAutoHome(){
  String autoWord = "False";
  if (autoHome == true){
    autoHome = false;
  }
  else{
    autoHome = true;
  }
  if (autoHome == true){
    autoWord = "True";
  }
  else{
    autoWord = "False";
  }
  Serial.println("AutoHome ON: " + autoWord);
}
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

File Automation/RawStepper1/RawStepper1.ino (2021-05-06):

/*
 * This sketch is designed to demonstrate the step functions
 * using a 4-wire bipolar stepper motor. A related sketch will
 * use the ULN2003 stepper driver instead of just the Arduino.
 * This is an example of simple "Wave Driving"
 */

 // Variables
 #define STEPPER_PIN_1  8
 #define STEPPER_PIN_2  9
 #define STEPPER_PIN_3  10
 #define STEPPER_PIN_4  11
 int step_number = 0;     // keeps track of the step count
 int theDelay = 10;        // global delay in milliseconds
// boolean dir = true;    // keeps track of the current direction
// byte charIn = 49;      // holds the value read on the serial bus
// int speed = 100;       // speed of the stepper, initial is MAX of 10

void setup() 
{
  pinMode(STEPPER_PIN_1, OUTPUT);
  pinMode(STEPPER_PIN_2, OUTPUT);
  pinMode(STEPPER_PIN_3, OUTPUT);
  pinMode(STEPPER_PIN_4, OUTPUT);
  //Serial.begin(9600);
}

void loop() 
{
  for(int a = 0; a < 200; a++)  // 15 deg/step = 360/15=24 iterations for one rev
  {
    OneStep(false);   //CW
    delay(theDelay);
  }
  for (int a = 0; a < 200; a++)
  {
    OneStep(true);    // CCW
    delay(theDelay);
  }
}

void OneStep(bool dir)
{
  if(dir == true) // CW
  {
    switch (step_number)
    {
      case 0:
        digitalWrite(STEPPER_PIN_1,HIGH);
        digitalWrite(STEPPER_PIN_2,LOW);
        digitalWrite(STEPPER_PIN_3,LOW);
        digitalWrite(STEPPER_PIN_4,LOW);
        break;
      case 1:
        digitalWrite(STEPPER_PIN_1,LOW);
        digitalWrite(STEPPER_PIN_2,HIGH);
        digitalWrite(STEPPER_PIN_3,LOW);
        digitalWrite(STEPPER_PIN_4,LOW);
        break;
      case 2:
        digitalWrite(STEPPER_PIN_1,LOW);
        digitalWrite(STEPPER_PIN_2,LOW);
        digitalWrite(STEPPER_PIN_3,HIGH);
        digitalWrite(STEPPER_PIN_4,LOW);
        break;
       case 3:
        digitalWrite(STEPPER_PIN_1,LOW);
        digitalWrite(STEPPER_PIN_2,LOW);
        digitalWrite(STEPPER_PIN_3,LOW);
        digitalWrite(STEPPER_PIN_4,HIGH);
        break;
    }
  }
    else  // CCW
    {
      switch(step_number)
      {
        case 0:
          digitalWrite(STEPPER_PIN_1,LOW);
          digitalWrite(STEPPER_PIN_2,LOW);
          digitalWrite(STEPPER_PIN_3,LOW);
          digitalWrite(STEPPER_PIN_4,HIGH);
          break;
        case 1:
          digitalWrite(STEPPER_PIN_1,LOW);
          digitalWrite(STEPPER_PIN_2,LOW);
          digitalWrite(STEPPER_PIN_3,HIGH);
          digitalWrite(STEPPER_PIN_4,LOW);
          break;
        case 2:
          digitalWrite(STEPPER_PIN_1,LOW);
          digitalWrite(STEPPER_PIN_2,HIGH);
          digitalWrite(STEPPER_PIN_3,LOW);
          digitalWrite(STEPPER_PIN_4,LOW);
          break;
        case 3:
          digitalWrite(STEPPER_PIN_1,HIGH);
          digitalWrite(STEPPER_PIN_2,LOW);
          digitalWrite(STEPPER_PIN_3,LOW);
          digitalWrite(STEPPER_PIN_4,LOW);
          break;
    }
  }
  step_number++;
  if (step_number > 24)
  {
    step_number = 0;
  }
  delay(theDelay);
}

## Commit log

2019-04-13 Add files via upload
    This is a modified STL file for oval aperture masks for the OVIO holder.
    [07_rotery_section_gratingholder_25x25x6_tom.stl]
2019-04-30 Add files via upload
    The 17_2ovio_slit_disc.* files are ones that have been modified to completely utilize the size of the OVIO slits. By Thomas C. Smith.
    [17_2ovio_holder_slit_disc.stl]
2019-05-13 Amazon URL to Steppers w/ UNL2003 Drivers
2019-07-08 Create Using the Relco SC480 calibration lamp.docx
2020-03-10 LHiRes III lamps controller
    This sketch is used for controlling the LHiRes III spectrographs various lamps. Additionally it is written to allow for local LED indication of the various lamp status' as an option.
2020-03-17 Add files via upload
    Parts to move a small mirror into the LowSpec light path for illuminating the slit with Cal/flat light
    [Motor Gear.STL, RushGears_2017_S2020.STL, motor box.STL]
2020-03-17 Create Calibration system parts
2020-03-18 Add files via upload
    This is a system of parts that will move a small mirror 10mm into the light path so that cal/flat illumination is directed into the slit.
    [Box cover.STL, Motor Gear.STL, RushGears_2017_S2020.STL, motor box.STL]
2020-03-18 Removing files in wrong location.
    [Motor Gear.STL, RushGears_2017_S2020.STL, motor box.STL]
2020-03-18 Add files via upload
    Arduino Sketch to control the motor
2020-03-19 Add files via upload
    Control and voltage requirements for the LowSpec
    [LowSpec control.xlsx]
2020-03-20 Added a the RS232 and comments on some of the interfaces.
    [LowSpec control.xlsx]
2020-03-20 Initial basic case study. Modify as the case develops.
2020-03-20 Initial Case Studies.
2020-03-24 Added a snapshot of the Google Doc spreadsheet for planning and resources.
    [GoogleDoc_3DSpectroPlanningResouces.xlsx]
2020-04-20 3D Printing and Web search starter
2020-04-21 Tom added more stuff.
    [GoogleDoc_3DSpectroPlanningResouces.xlsx]
2020-04-24 Add files via upload
    A spread sheet to determine FOV of guide cameras on reflective slit.
    [Guide camera FOV.xlsx]
2020-05-05 Stepping the 48BYJ-28 stepper motor without a drive board
2020-05-26 taper block with 2 degree taper and a T2 hole
    [Outside taper block.STL]
2020-06-02 Polycase AL48P-01 box
    [AL-xxB_AL-48BP-01.STL]
2020-07-03 Add files via upload
    This sketch moves the 28BYJ-48 stepper motor to a position that is input from the serial port. The final move is always in the same direction to eliminate backlash.
2020-07-10 Zipped file of sketches and programs
    This zipped file contains lots of sample and completely functional Arduino sketches and Python3 programs to use as we develop the NA1 spectroscope.
    Thomas C. Smith
2020-07-28 Add files via upload
    This is the threaded rod with a 3mm x 10mm pocket for the magnet.
    [threaded post-M.STL]
2020-08-03 Added a tex filder to avoid doc in case we want Sphinx. Added an article to the tex folder.
2020-08-03 Cleaned up the github.
    [CAL01_BoitierV2.stl, CAL02_coulant 31_75_V2.stl, CAL03_support_miroir.stl, CAL04_T42mm.stl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]
2020-08-07 Ver.1 of Calibration Injector
    This sketch is fairly well self documenting and include lots of in-line comments.
    Python3 GUI program will be added once completed. 20200807
2020-08-07 Enhanced version with PWM for slit control
    This revised code has the same name as the original so don't be fooled.
    I added PWM capability when operating the slit LED.
2020-08-11 Added section with mirror makers formula.
    [Gerber_BoardOutline.GKO, Gerber_BottomLayer.GBL, Gerber_BottomPasteMaskLayer.GBP, Gerber_BottomSolderMaskLayer.GBS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]
2021-01-26 Arduino sketches for use a guides.
    These are sketches that show a method of creating a non-blocking delay and another sketch to show how one might use interrupts on the Arduino.
2021-02-14 Modified interrupt Arduino code
    This code was modified to better test the interrupt capability of the Arduino.
2021-07-14 Local changes
    [CAL01_BoitierV2.stl, CAL02_coulant 31_75_V2.stl, CAL03_support_miroir.stl, CAL04_T42mm.stl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]
